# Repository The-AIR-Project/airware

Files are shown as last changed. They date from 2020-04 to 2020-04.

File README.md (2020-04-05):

# AIRware
Files for the AIR project.

#### External Libraries

LiquidCrystal_I2C (https://github.com/fdebrabander/Arduino-LiquidCrystal-I2C-library/blob/master/LiquidCrystal_I2C.h)

#### How To Use

If the software is loaded as is onto the Arduino, and the:
- One button (black, on our design) cycles through age group settings
    - These can only be toggled while ventilation is not in progress
- Potentiometers adjust volume, pressure, and rate settings
    - These can be adjusted at any time
    - Volume measurements are calibrated as explained below
- If the airway is blocked, the servo will draw too much current and a blockage
is predicted (see how to calibrate this below)  

#### Volume Output Characterization

- Record volume outputs at various servo angles
- In `scripts/volume_character.py`, place these values into `raw_vol` and `raw_ang`
- Take the average volume output at each servo angle, place these values into
`vol` and `ang`
- If any validation takes place, place these volumes and servo angles into
`val_vol` and `val_ang`
- Note: the `ang_to_vol` function was determined by fitting a cubic to the
volume output vs servo angle data in Excel

#### Blockage Detection Characterization

- Blockage detection is only implemented in adults right now
- Any adjustments to mechanical design requires recalibration
- To calibrate, output the volume, pressure, and `current_sum` value upon releasing the bag (around line 400 or so)
- Save this data in Excel in the format shown in `current_data.xlsx`, which contains
the most recently-used data for characterization
- Run `scripts/current_character.py` to fit a surface function to the data and output the
coefficients `[a, b, c, d, e, f]`
    - polynomial of the form `z = a + bx + cx^2 + dy + ey^2 + fxy`
- Apply these coefficients in  `predict_current()` function

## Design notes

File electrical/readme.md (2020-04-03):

# Electrical Schematic

`electrical.pdf` contains a simple diagram showing necessary connections for the
electrical aspect of our design.
- The only power requirements is that it's able to supply the Arduino with
7-12V, the servo with 6.8V, and supply up to 3A (anything above 2.5A <i>should</i>
be okay, but we went with 3A to be safe)
    - If you use a different MCU or motor, just make sure you meet its specs of
    course
- The 220 ohm resistors on the LEDs can be any value that works for you
    - the red LED we used should have gotten a larger resistor, which is why
    in the code it is being powered by PWM (it was too bright!)

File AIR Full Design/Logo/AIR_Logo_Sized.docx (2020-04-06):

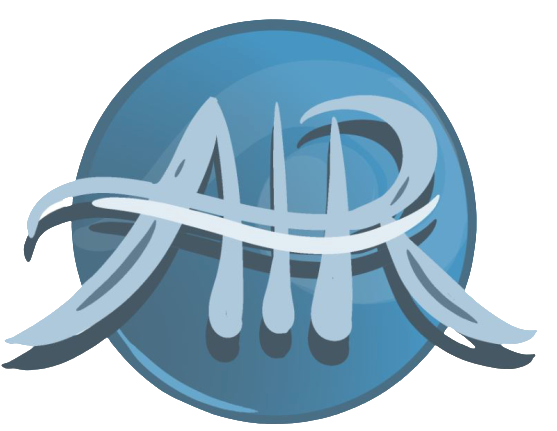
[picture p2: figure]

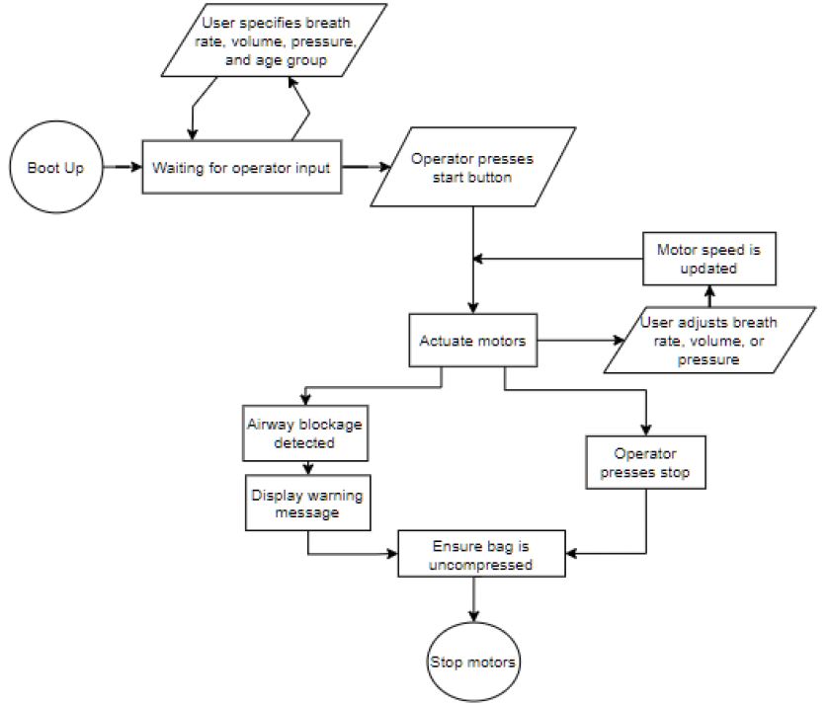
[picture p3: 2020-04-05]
final_code/flowchart.JPG

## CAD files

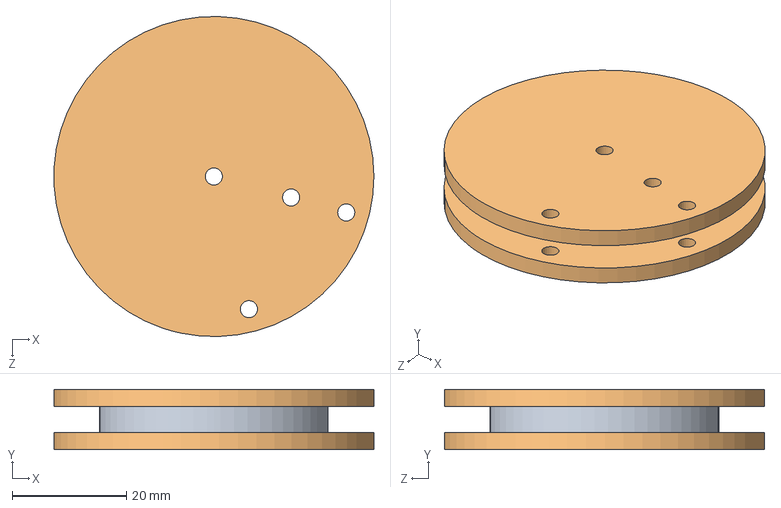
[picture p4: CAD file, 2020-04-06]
AIR Full Design/Spool_Assembly.SLDASM
56.0 x 10.5 x 56.0 mm
Servo_Spool_Inside
Servo_Spool_Outside x 2

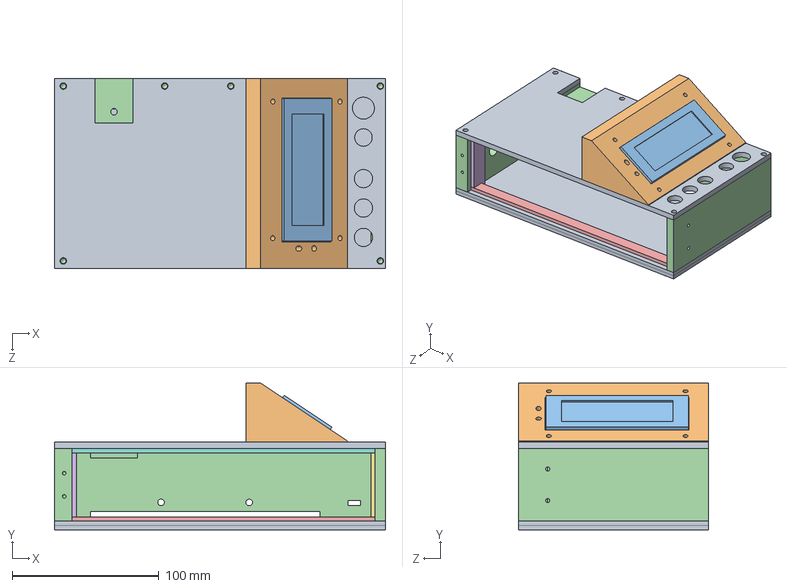
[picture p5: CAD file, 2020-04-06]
AIR Full Design/Control Box V4/Control_Box_V4.SLDASM
225.2 x 100.0 x 129.0 mm
Control Box Top
Screen_Mount
LCD_Screen
Box Frame
Door_Frame_Bottom
Door_Frame_Left
Door_Frame_Right
Door_Frame_Top
Control Box Bottom x 2

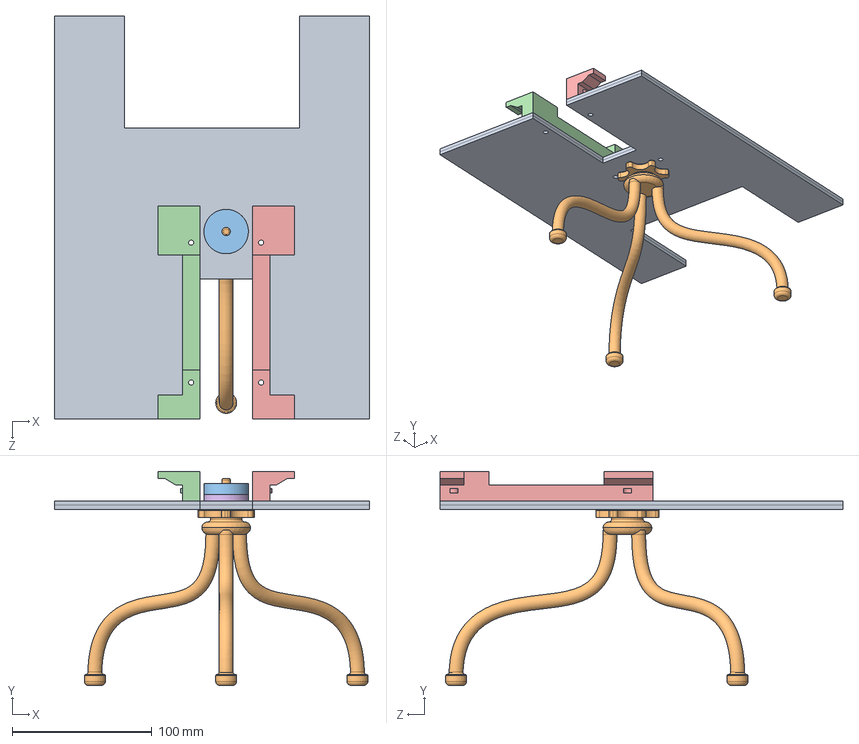
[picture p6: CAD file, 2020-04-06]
AIR Full Design/Mounting Stand/Mount_Interface_Assembly.SLDPRT.SLDASM
225.2 x 153.0 x 288.1 mm
Mount_Interface_Plate x 2
Mount_Interface_Tripod
Mount_Interface_Securement_Disk
Mount_Interface_Finger_Left
Mount_Interface_Finger_Right
Mount_Interface_Spacer

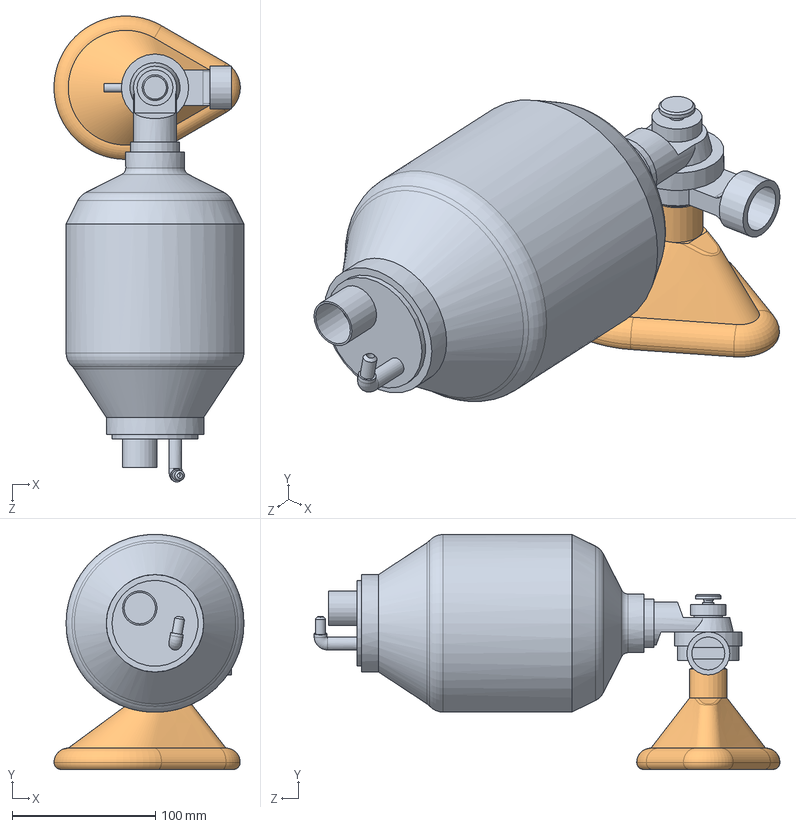
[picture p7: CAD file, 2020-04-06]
AIR Full Design/Bag Valve Mask/Bag_Valve_Mask.SLDASM
132.5 x 163.9 x 325.0 mm
Bag_Adult
Mask_Updated

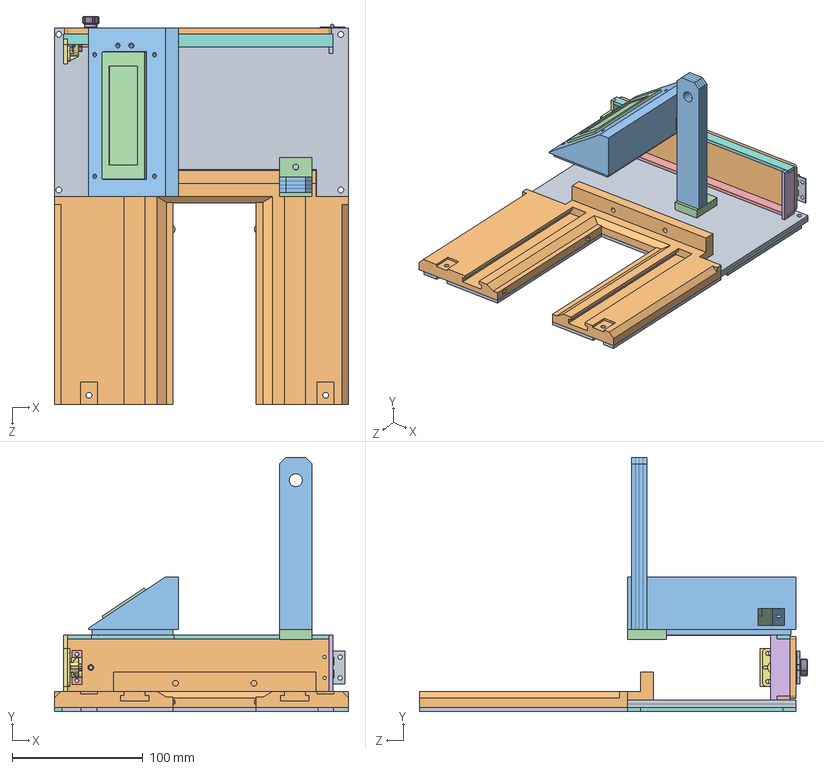
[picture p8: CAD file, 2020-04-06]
AIR Full Design/Base_Structure_Assembly.SLDASM
225.3 x 194.5 x 296.8 mm
Base_Frame_V3
Screen_Mount
LCD_Screen
Door_Frame_Bottom
Door_Frame_Left
Door_Frame_Right
Door_Frame_Top
Control Box Bottom x 2
Door_Hinge
Control_Box_Door
Tensioner End Support_Layer x 4
Tensioner End Support_Bottom
Door_Latch_Strike
Door_Knob_Small
Door_Latch_Plate
Control_Box_Spacer
Frame_Spacer

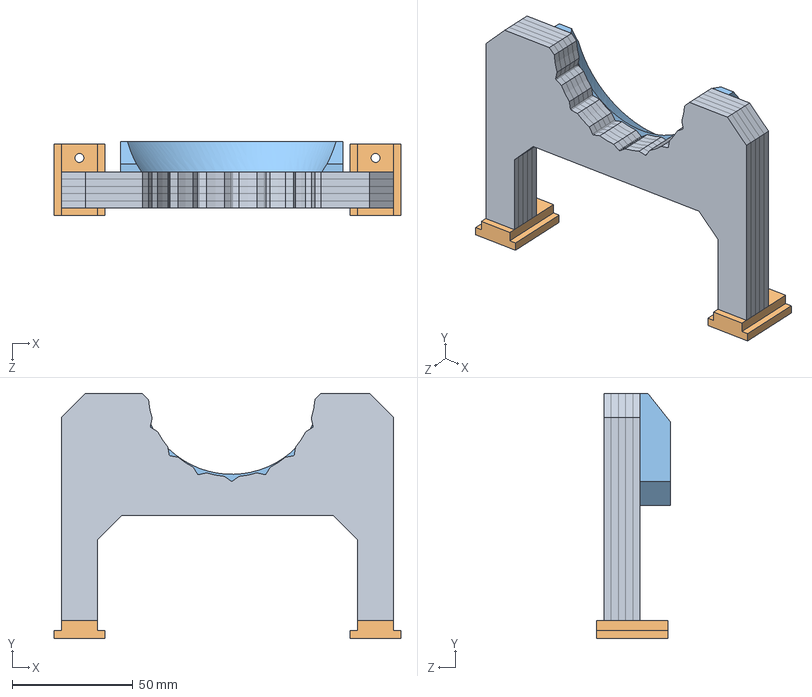
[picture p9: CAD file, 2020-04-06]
AIR Full Design/Back Support Assembly.SLDASM
143.5 x 101.5 x 30.5 mm
Back Support Layer x 5
Back Support Feet x 2
Bag Pullout Support

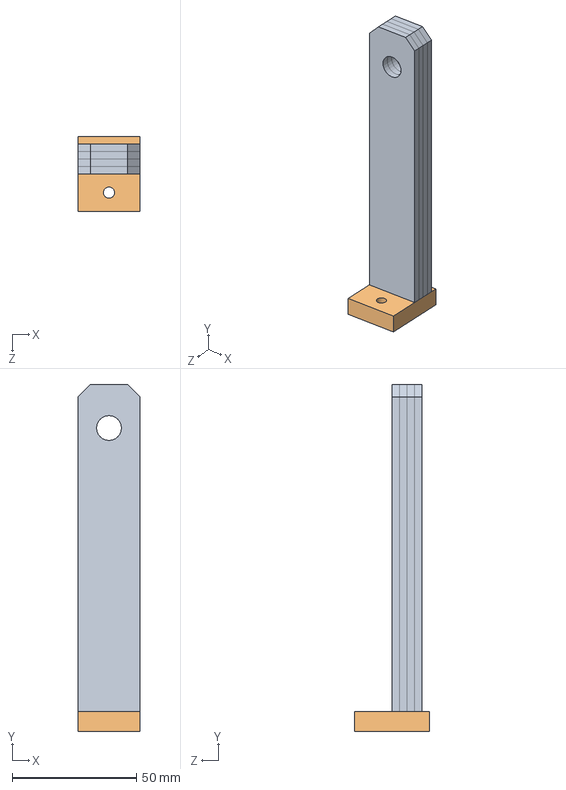
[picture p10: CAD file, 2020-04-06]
AIR Full Design/Tensioner End Support_Assembly.SLDASM
25.0 x 139.5 x 30.0 mm
Tensioner End Support_Layer x 4
Tensioner End Support_Bottom

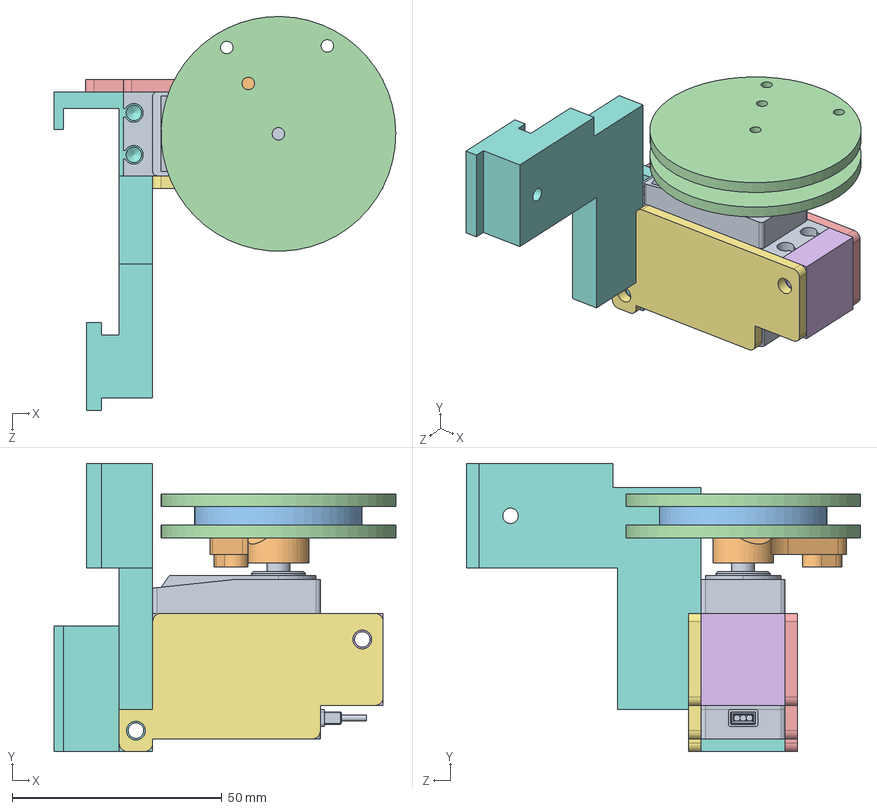
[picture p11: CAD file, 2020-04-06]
AIR Full Design/Servo_Assembly.SLDASM
81.5 x 68.8 x 94.0 mm
Servo
Servo_Arm
Servo_Spool_Inside
Servo_Spool_Outside x 2
Servo_Mount_Plate
Servo_Mount_Block_Top
Servo_Mount_Plate_2
Servo_Mount_Block_Bottom_V4

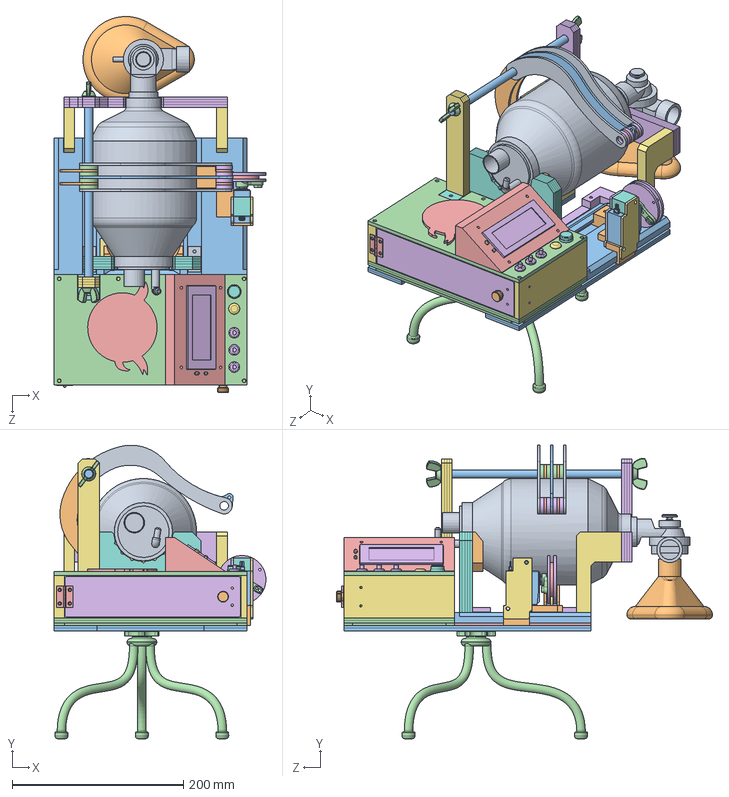
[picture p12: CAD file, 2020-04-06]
AIR Full Design/Full Design_V4.SLDASM
247.2 x 342.4 x 438.7 mm
Bag_Adult
Mask_Updated
Base_Frame_V3
Control Box Top
Screen_Mount
LCD_Screen
Box Frame
Door_Frame_Bottom
Door_Frame_Left
Door_Frame_Right
Door_Frame_Top
Control Box Bottom x 2
Door_Hinge
Control_Box_Door
Tensioner End Support_Layer x 4
Tensioner End Support_Bottom
Door_Latch_Strike
Door_Knob_Small
Door_Latch_Plate
Control_Box_Spacer
Frame_Spacer
Front Support Layer x 4
Front Support Side Legs x 2
Back Support Layer x 5
Back Support Feet x 2
Bag Pullout Support
Servo
Servo_Arm
Servo_Spool_Inside
Servo_Spool_Outside x 2
Servo_Mount_Plate
Servo_Mount_Block_Top
Servo_Mount_Plate_2
Servo_Mount_Block_Bottom_V4
Tensioner_Rod
M10 Wing nut x 2
Logo_Badge__Reference_Only
Potentiometer x 3
Button_Age
Button_Start_Stop
Green_LED
Red_LED
Mount_Interface_Plate x 2
Mount_Interface_Tripod
Mount_Interface_Securement_Disk
Mount_Interface_Finger_Left
Mount_Interface_Finger_Right
Mount_Interface_Spacer
Compression_Arm_Top__Reference_Only x 2
Compression_Arm_Bottom__Referencce_Only x 2
Compression_Arm_Top_With_Connector__Reference_Only
Tensioner_Rod_Spacer x 4
Compression_Arm_Spacer_Thin x 2
Compression_Arm_Spacer x 6
Compression_Arm_Bottom_Connector__Reference_Only

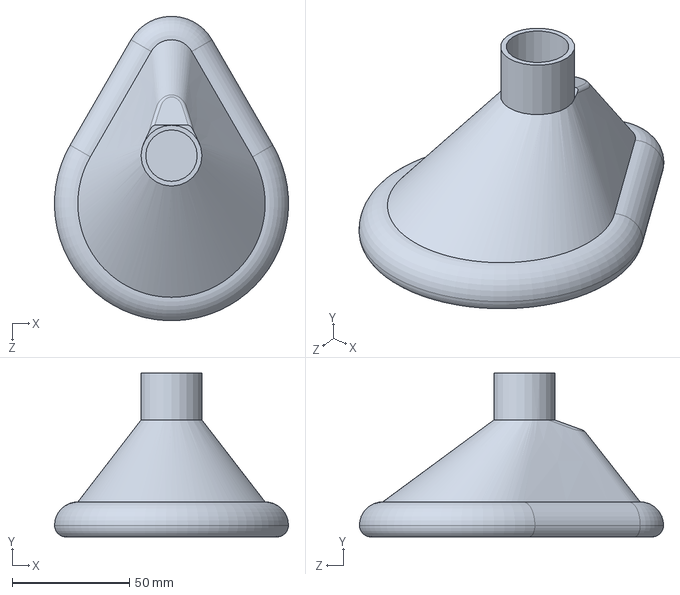
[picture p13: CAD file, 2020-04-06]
AIR Full Design/Bag Valve Mask/Mask_Updated.SLDPRT
99.9 x 70.0 x 129.9 mm

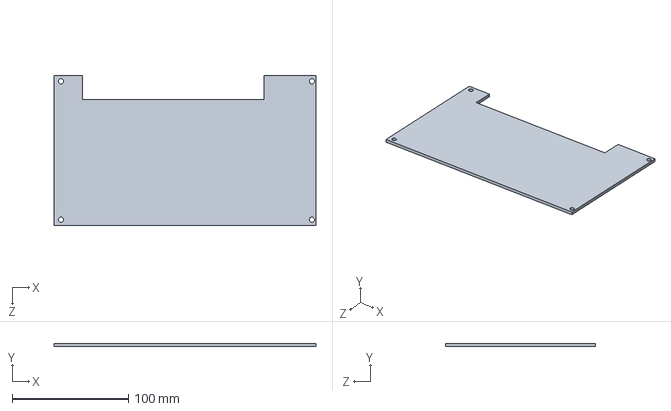
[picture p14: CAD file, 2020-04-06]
AIR Full Design/Control Box V4/Control Box Bottom.SLDPRT
225.2 x 3.00 x 129.0 mm

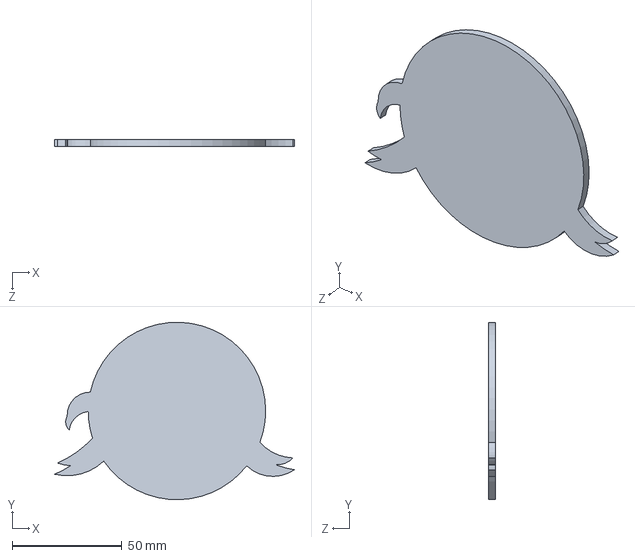
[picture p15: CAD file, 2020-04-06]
AIR Full Design/Logo/Logo_Badge__Reference_Only.SLDPRT
109.6 x 81.0 x 3.00 mm

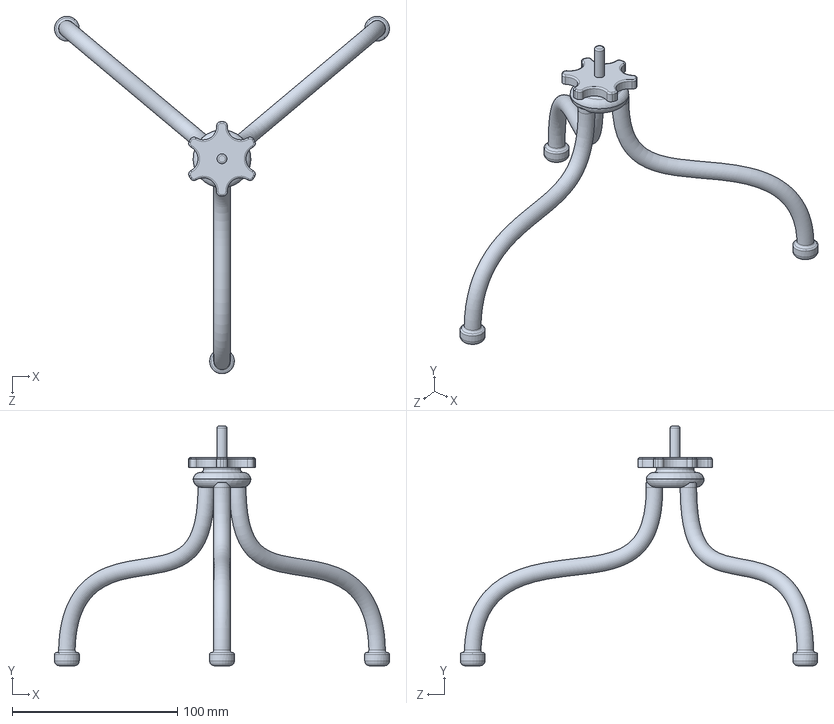
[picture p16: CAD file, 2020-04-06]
AIR Full Design/Mounting Stand/Mount_Interface_Tripod.SLDPRT
202.7 x 145.0 x 216.2 mm

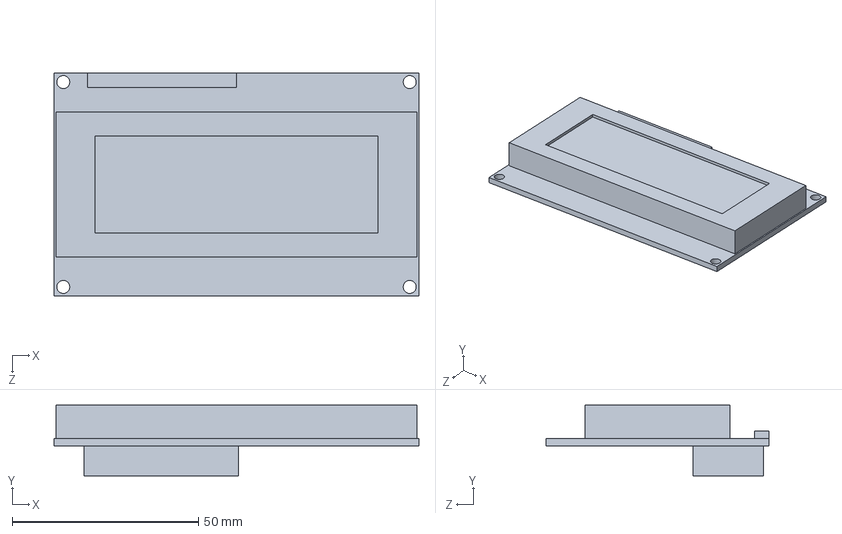
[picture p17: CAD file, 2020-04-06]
AIR Full Design/Stand In Models for Purchased Parts/LCD_Screen.SLDPRT
98.0 x 19.0 x 60.0 mm

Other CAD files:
AIR Full Design/Front Support Assembly.SLDASM
AIR Full Design/AutoCad Files For Reference Parts/Compression Arm Components_4point5mm.dwg
AIR Full Design/AutoCad Files For Reference Parts/Compression Arm Components_3mm.dwg
AIR Full Design/Bag Valve Mask/Bag_Infant.SLDPRT
AIR Full Design/AutoCad Files For Reference Parts/Logo_Badge.DWG
AIR Full Design/Back Support Feet.SLDPRT
AIR Full Design/Back Support Layer.SLDPRT
AIR Full Design/Bag Pullout Support.SLDPRT
AIR Full Design/Bag Valve Mask/Bag_Adult.SLDPRT
AIR Full Design/Base_Frame_V3.SLDPRT
AIR Full Design/Compression_Arm_Bottom_Connector__Reference_Only.SLDPRT
AIR Full Design/Compression_Arm_Bottom__Referencce_Only.SLDPRT
AIR Full Design/Compression_Arm_Spacer.SLDPRT
AIR Full Design/Compression_Arm_Spacer_Thin.SLDPRT
AIR Full Design/Compression_Arm_Top_With_Connector__Reference_Only.SLDPRT
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

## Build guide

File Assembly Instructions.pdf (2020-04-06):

# Automatic Inhalation Resuscitator

# Assembly Instructions

Originally developed by Connor Simmons, Sam Raisbeck, Brian Mao, and Aditya Matam from The University of Waterloo

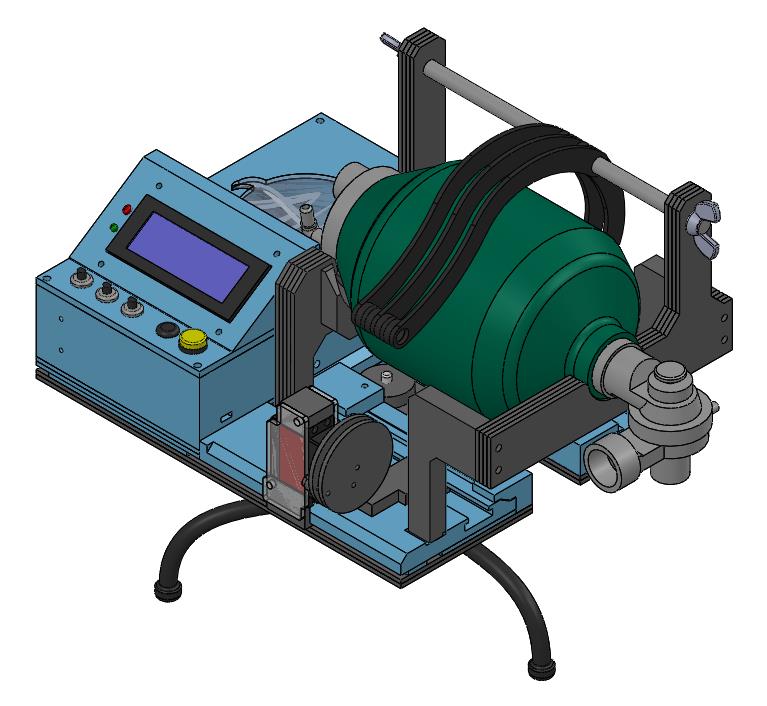
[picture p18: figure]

**Disclaimer: The following assembly instructions are made only as a general guide to construct the version of AIR most recently completed as of April 5, 2020. As this product will be manufactured quickly, components may be modified or exchanged to fit your specific needs. Any modifications made to the design or its components may result in required variations to the assembly.

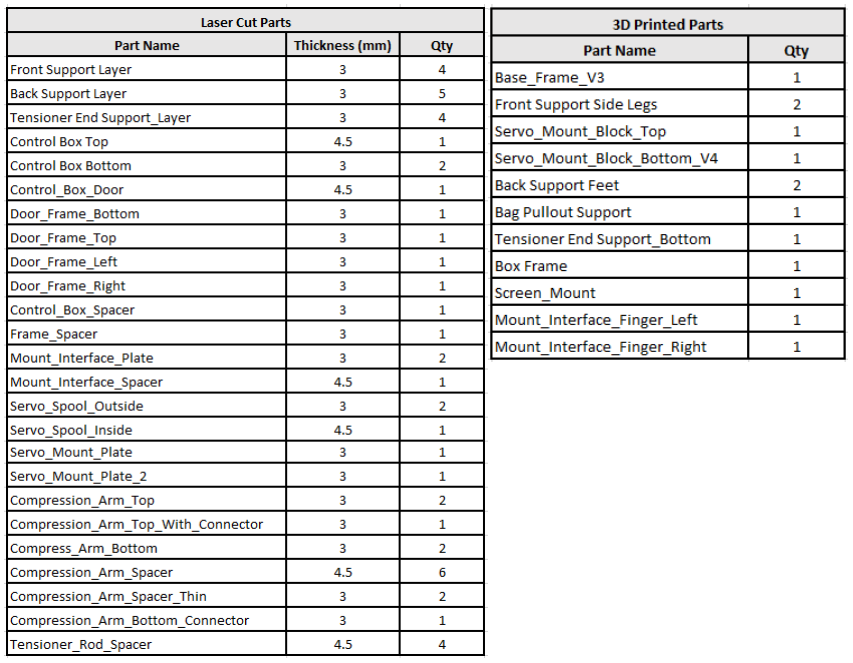
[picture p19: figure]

https://the-air-project.github.io/

Note 1: Please download the entire “Air Full Design” folder, and open the main assembly: “Full Design_V4”

Note 2: Within the provided 3D CAD model, the compression arm models are reference only. This includes the three top arms, two bottom arms, and the bottom arm connector. The dimensions used for the models are reference only and do not fully represent the final manufactured versions. These files are tagged with a “Reference_Only” at the end of the file name.

Note 3: Accurate drawing files for “Reference Only” components can be found in the “AutoCad files” folder. These files are the true manufactured versions for these components. This also includes the logo badge

Note 4: All other components were manufactured according to the dimensions in the CAD model. All dimensions are in mm.

AIR was manufactured using a mixture of 3D printed plastic components, as well as laser cut acrylic. The breakdown of 3D printed vs. laser cut components is listed below. The thickness of acrylic components is also listed, along with a required quantity for each component. The material selections were made with interest to cost and manufacturing time. More complex components were 3D printed, but laser cutting acrylic is often faster and less expensive. Any variations to the materials used is up to manufacturer discretion.

## 1 – Control Box

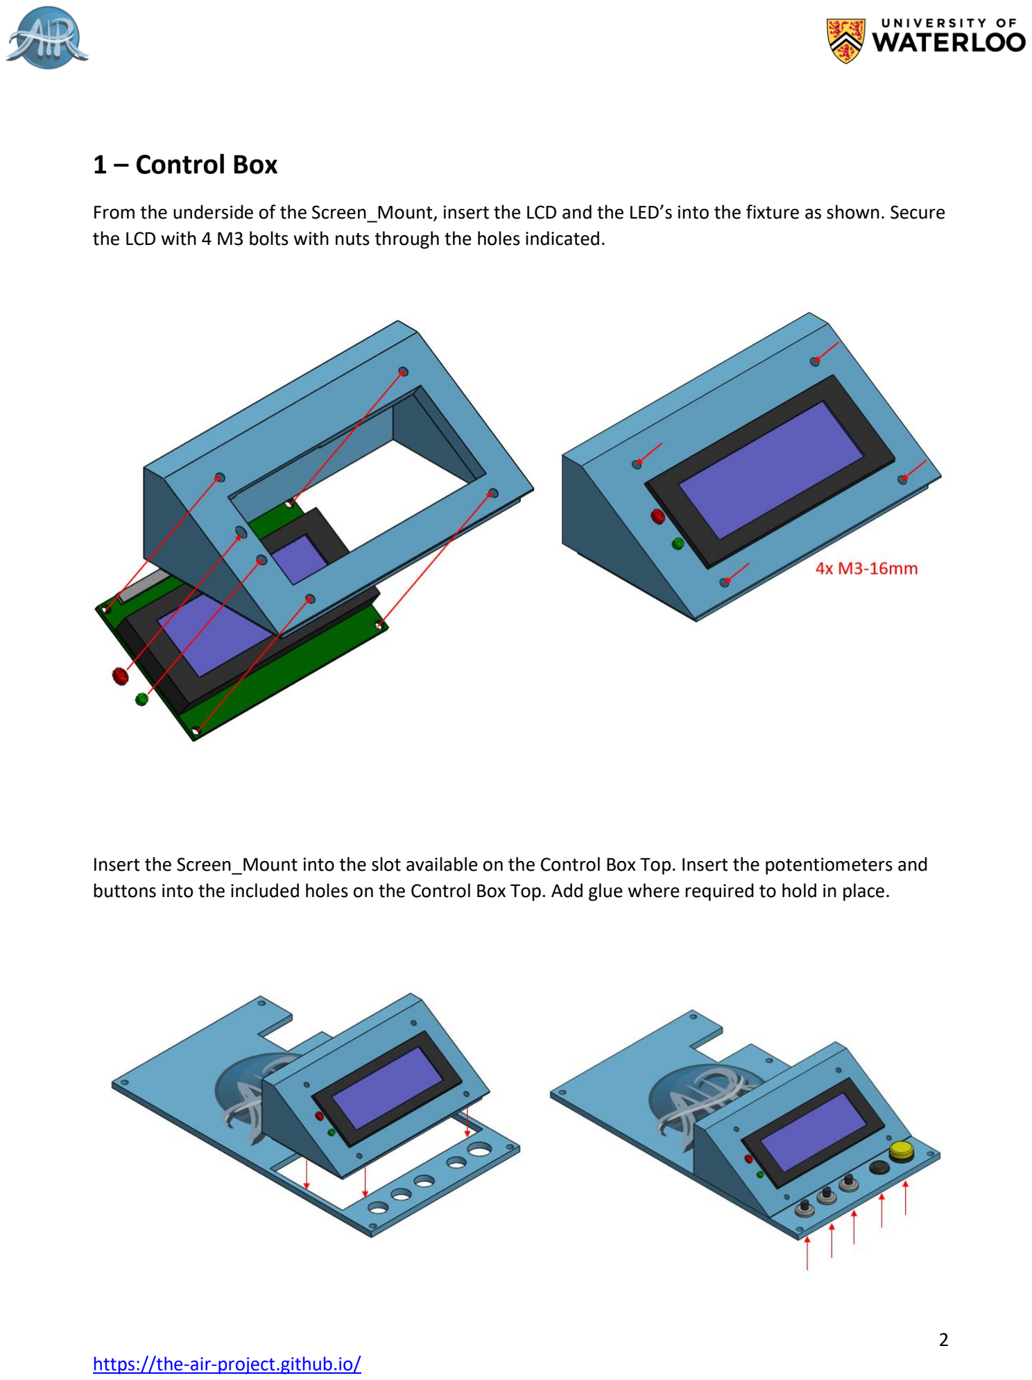
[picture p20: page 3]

From the underside of the Screen_Mount, insert the LCD and the LED’s into the fixture as shown. Secure the LCD with 4 M3 bolts with nuts through the holes indicated.

Insert the Screen_Mount into the slot available on the Control Box Top. Insert the potentiometers and buttons into the included holes on the Control Box Top. Add glue where required to hold in place.

Attach the Control Box Top to the Box Frame through the 6 screw holes indicated.

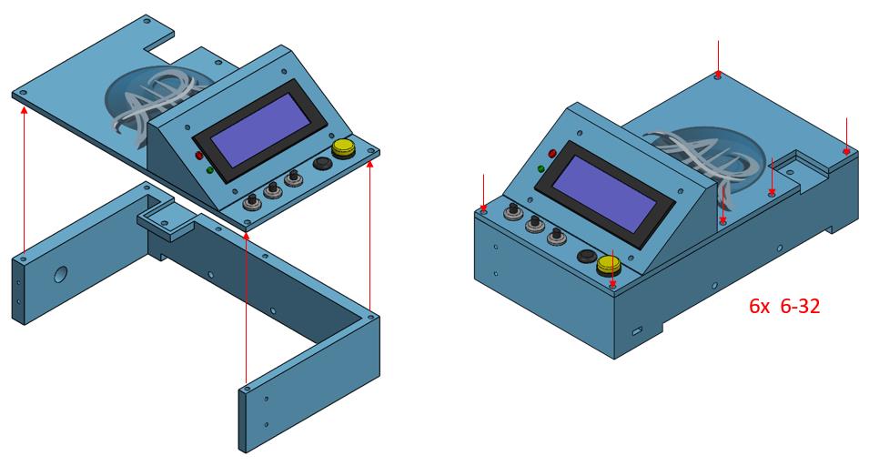
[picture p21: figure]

At this point it is recommended that the control box electronics be fully wired. This includes the connections from the controls to the Arduino, the power supply connector, current, sensor, etc. These connections can be found in our electrical schematic, which is also available for download. A rear view of the control box is included below to indicate the use for the cut-outs on the box frame

Attach 2 layers of the Control Box Bottom in the manner shown to the underside of the control box, through the 4 screw holes indicated.

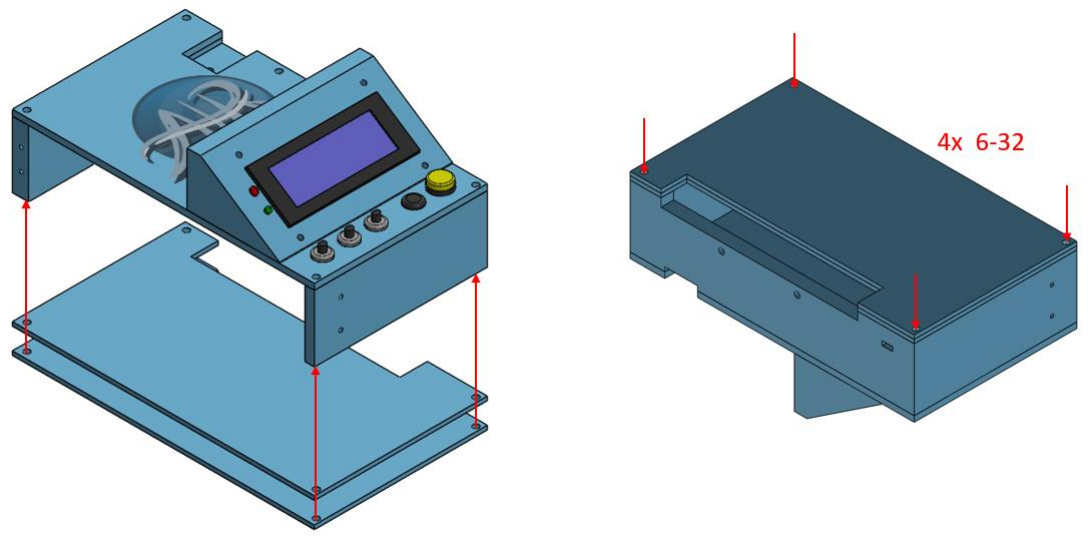
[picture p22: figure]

Place the Door_Frame_Bottom inside the control box, 4.5mm back from the edge of the Control Box Bottom. Add glue where required to hold in place. Repeat for the Door_Frame_Left, Door_Frame_Right, and Door_Frame_Top. If the bottom frame was installed correctly, the remaining frame pieces should fit together nicely with their included cut-outs. Check the placement and orientation of all pieces before

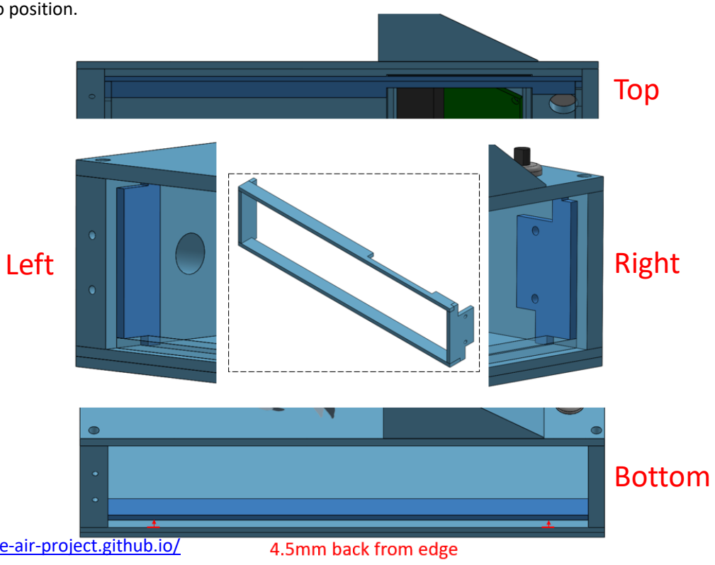
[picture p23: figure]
Left; Right; Top; Bottom

gluing into position.

Place the Door_Latch_Plate inside the control box on the Door_Frame_Left, and secure from the outside of the control box through the indicated screw holes with 2 M3 bolts with nuts.

On the Control_Box_Door, secure the Door_Latch_Strike using 2 M3 bolts, with nuts. Secure the Door_Knob_Small from the other side through the door with a nut. Attach one side of the Door_Hinge to the door with 2 M3 bolts, with nuts. Then, attach the other side of the hinge to the control box with 2 screws. All bolt heads should be on the outside of the door.

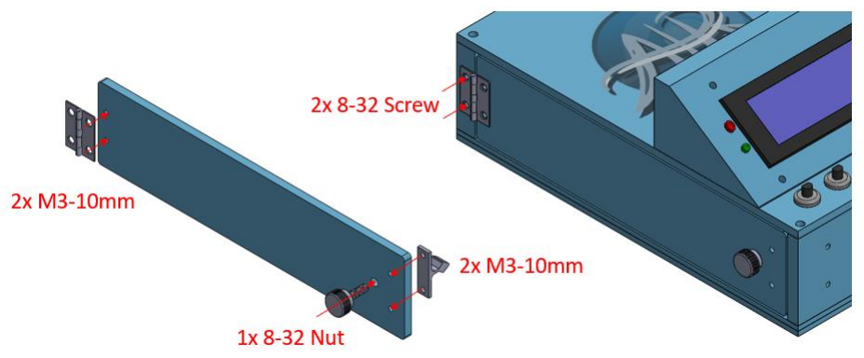
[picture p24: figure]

Available for download are our personal AIR logo and the AutoCad file for the logo badge. If willing, print and cut out the logo, and place on the control box with a little amount of glue. Then, place the logo badge overtop to protect the logo and provide a 3D effect. Add small drops of glue periodically around the perimeter of the badge once in place to secure. Only use small amounts around the outside as excess glue may seep underneath and effect the logo presentation.

The logo is sized properly in the AIR_Logo_Sized document.

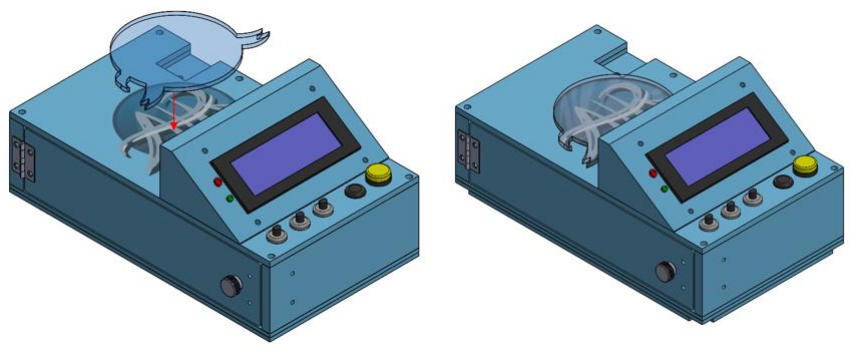
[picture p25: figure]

## 2 – Back Support Assembly

Place 5 Back Support Layers together, add glue where required to hold in place. Take special note that the support is NOT symmetric. The two top edges have slightly different lengths as indicated

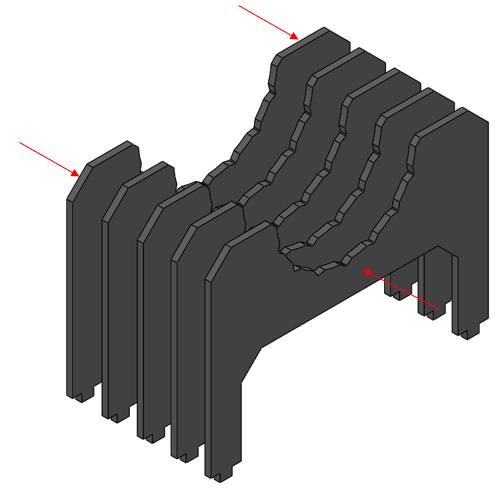
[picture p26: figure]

Take the combined layers and attach the 2 Back Support Feet by fitting the protruding nub on the bottom of the support legs into the notch on the feet as indicated. Note the orientation of the feet in relation to the edge lengths of the top of the support. Add glue to the notch to fully secure.

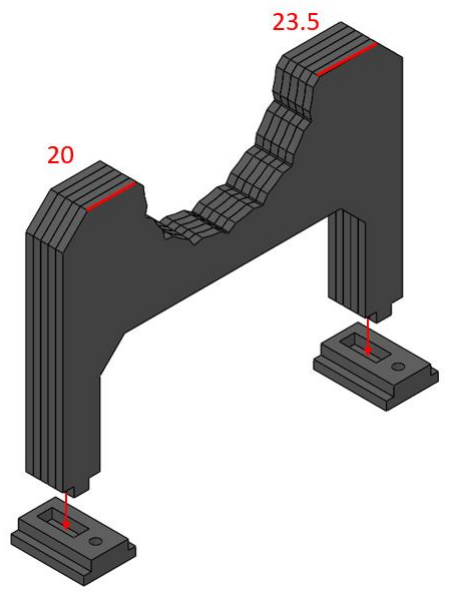
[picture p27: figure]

Attach the Bag Pullout Support to the support layers as indicated, add glue where required to hold in place. The flat edges at the top of the Pullout Support should be aligned with the top edge of the support layers as shown highlighted in blue.

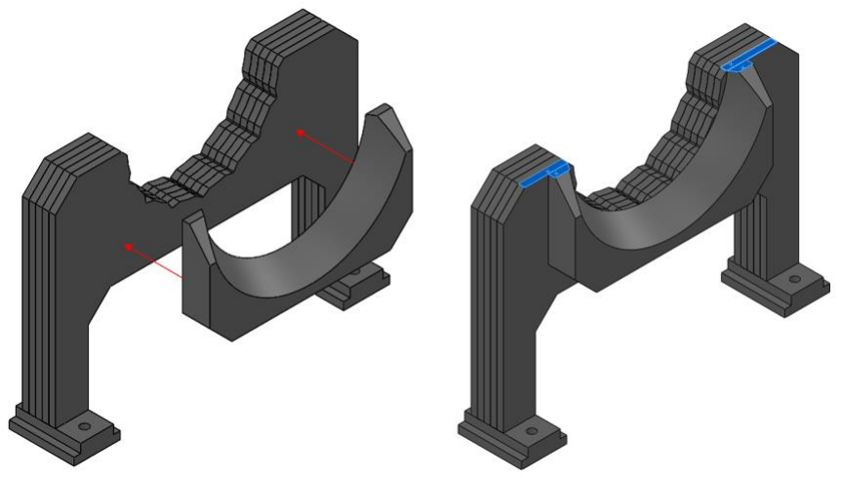
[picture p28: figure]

## 3 – Servo Assembly

Place the Servo_Mount_Block_Top and Servo_Mount_Block_Bottom_V4 on the servo in the positions shown. Secure in place using 4 screws in the locations shown, but DO NOT tighten fully.

Add the Servo_Mount_Plate in the position and orientation shown. Secure to the servo mount blocks in the indicated screw locations. Again, DO NOT tighten fully. Repeat for Servo_Mount_Plate_2. Once both plates are secure, go back and tighten all 8 screws.

To assemble the spool, take the servo arm and attach to a Servo_Spool_Outside, aligning the center of the servo arm with the center hole on the spool, and the furthest hole on the servo arm with the singular hole near the rim of the spool. Secure the arm using only the 1 screw provided with the arm in the hole furthest from the center. If a screw was not provided, an M3 bolt can be used

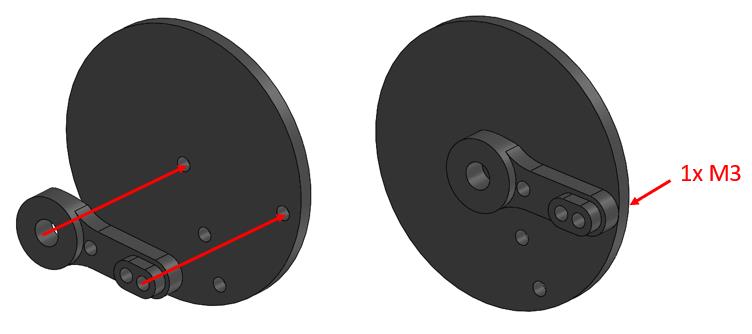
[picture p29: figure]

Next, place the Servo_Spool_Outside and servo arm pair together with another Servo_Spool_Outside on either side of a Servo_Spool_Inside. Align the set of 3 in-line holes as indicated. Secure the spool components together by 2 M3 bolts, with nuts. The bolt closer to the center will go through all 3 layers. The bolt near the outer rim goes through only the 2 outer spool layers.

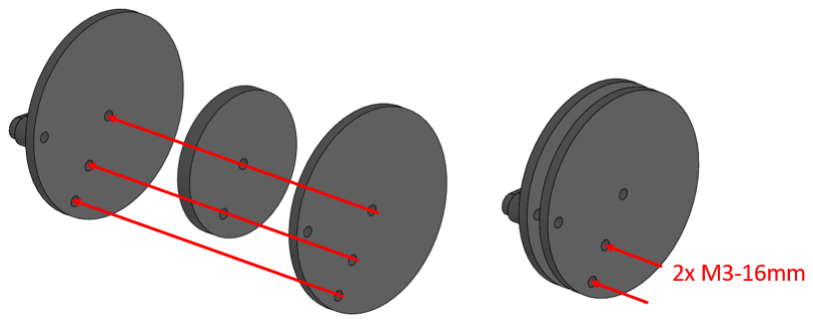
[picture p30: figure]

Attach the servo spool to the servo using the servo arm. Align the large center hole on the servo arm with the shaft of the servo. Secure the spool to the servo using an M3 bolt through the center hole on the spool as shown.

## 4 – Tensioner End Support Assembly

Place 4 Tensioner End Support Layers together, add glue where required to hold in place

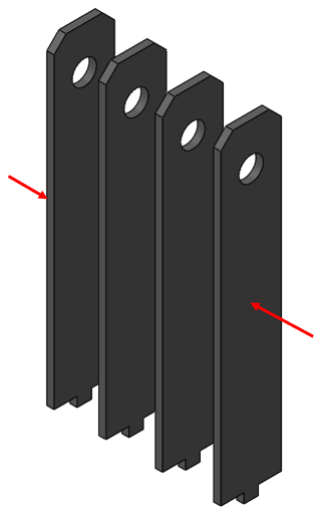
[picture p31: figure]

Take the combined layers and attach the Tensioner End Support_Bottom by fitting the protruding nub on the bottom of the support legs into the notch on the foot as indicated. Add glue to the notch to fully secure.

## 5 – Full Frame Assembly

Take the Base_Frame_V3 and insert into the open slot at in the front of the control box assembly from the underside. Secure the frame to the box using 2 bolts through the indicated holes and attach with nuts from the inside of the control box.

Insert the Tensioner End Support Assembly into the slot on the top of the control box. Secure to the box using 1 bolt through the Tensioner Support Assembly base, and attach a nut from the inside of the control box.

Take the Back Support Assembly and slide the support feet into the channels on the Base Frame as shown. Slide the support all the way to the end of the channel, or the approximate distance for the size of your Bag Valve Mask being used. Slide the Servo Assembly into the left side channel as shown. Insert the cable for the servo through the small square hole on the side of the control box.

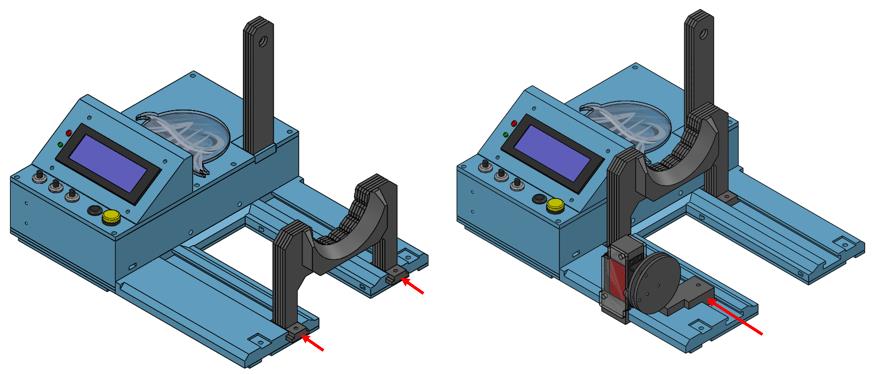
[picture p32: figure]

Take 2 Front Support Side Legs and insert them into the indented slots at the front of the Base Frame. Secure from the underside using 2 screws.

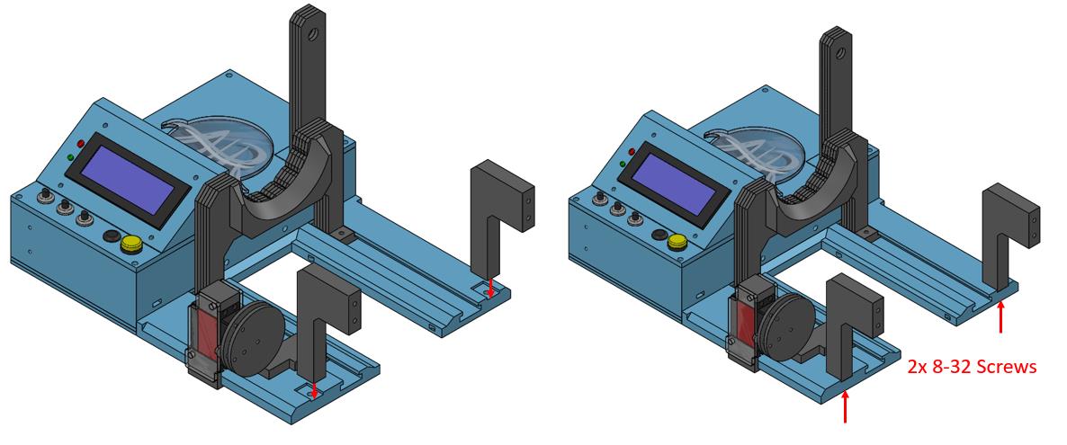
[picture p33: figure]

Place 4 Front Support Layers together against the Front Support Side Legs and secure from the front using 4 screws.

Align the Control Box Spacer and the Frame Spacer as shown on the underside of the frame. Add glue where required to hold in place

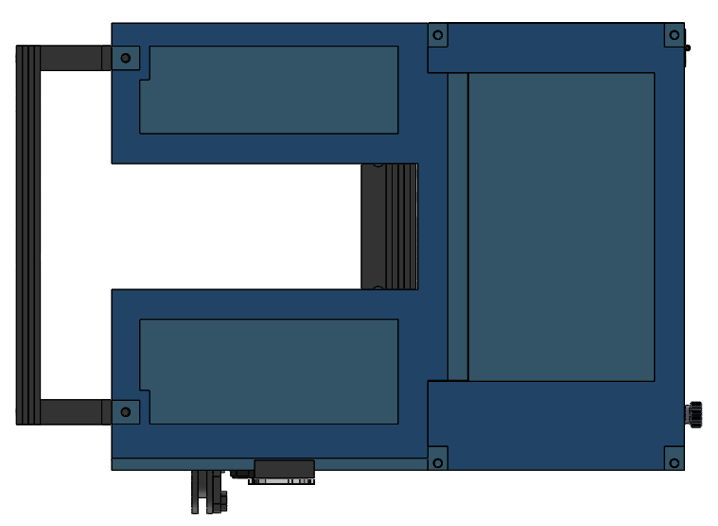
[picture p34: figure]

## 6 – Compression Arms

For the top compression arms, combine them together with the spacers only on the bottom side in the pattern shown. The compression arms must be arranged so the arm with the additional connector nub is in the middle, and the two regular arms the outside. In between, use 4 Compression_Arm_Spacers and 2 Compression_Arm_Spacer_Thin in the pattern indicated. Ensure all holes at both ends are aligned concentrically. Add glue where required to hold in place.

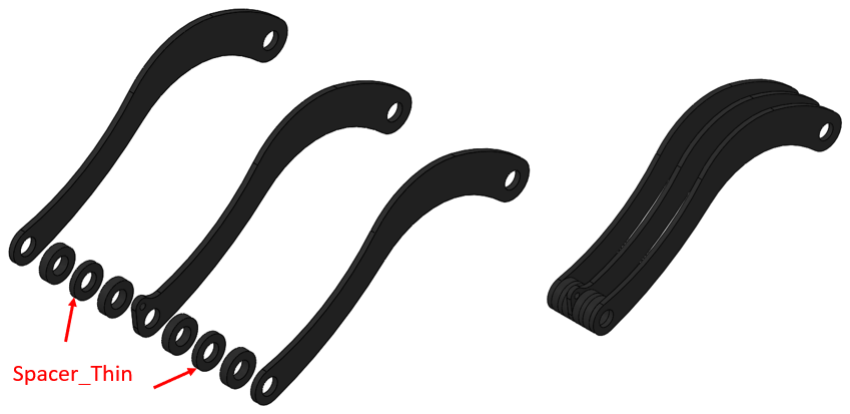
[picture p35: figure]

For the bottom compression arms, combine them together with the spacers only on the bottom side in the pattern shown. The compression arms are arranged on the outside, with the spacers and the additional connector in between. Use 2 Compression_Arm_Spacers and the connector piece in the pattern indicated. Ensure all holes at both ends are aligned concentrically. Add glue where required to hold in place.

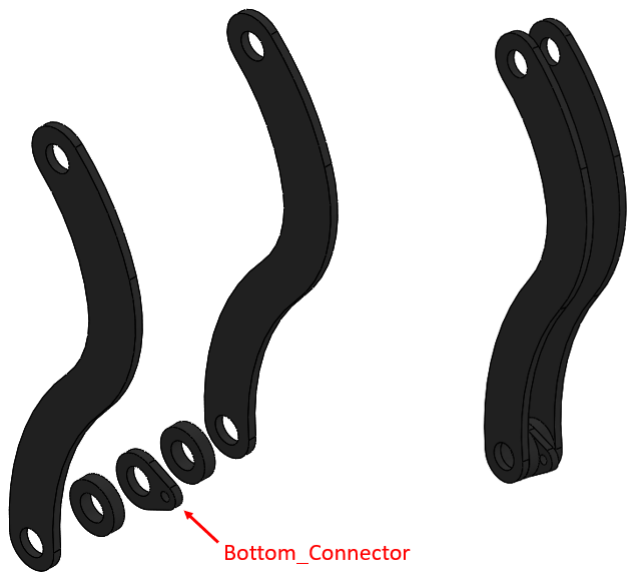
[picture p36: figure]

Slide the Tensioner_Rod through the hole in the Front Support Assembly. Add an O-ring before adding the combination of compression arm assemblies and spacers as shown. The 3 top compression arms and 2 bottom compression arms fit together at the open ends as shown, with a Tensioner_Rod_Spacer in between each arm (highlighted in dark blue between the black arms). It is important not to glue these spacers as they need to be free to rotate relative to each.

Note: The tensioner rod is 3/8” Aluminum, with 1-inch long threaded sections at the ends (3/8-16 thread)

Add another O-ring after the compression arm assemblies, and feed the tensioner rod though the tensioner end support assembly. Secure the rod in place at both ends with 2 wing nuts.

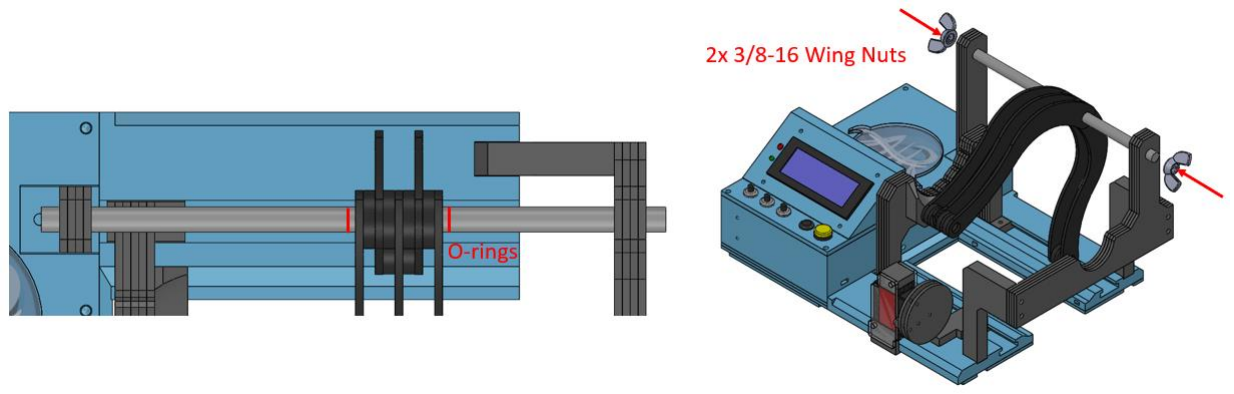
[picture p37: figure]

## 7 – Mount Interface Assembly

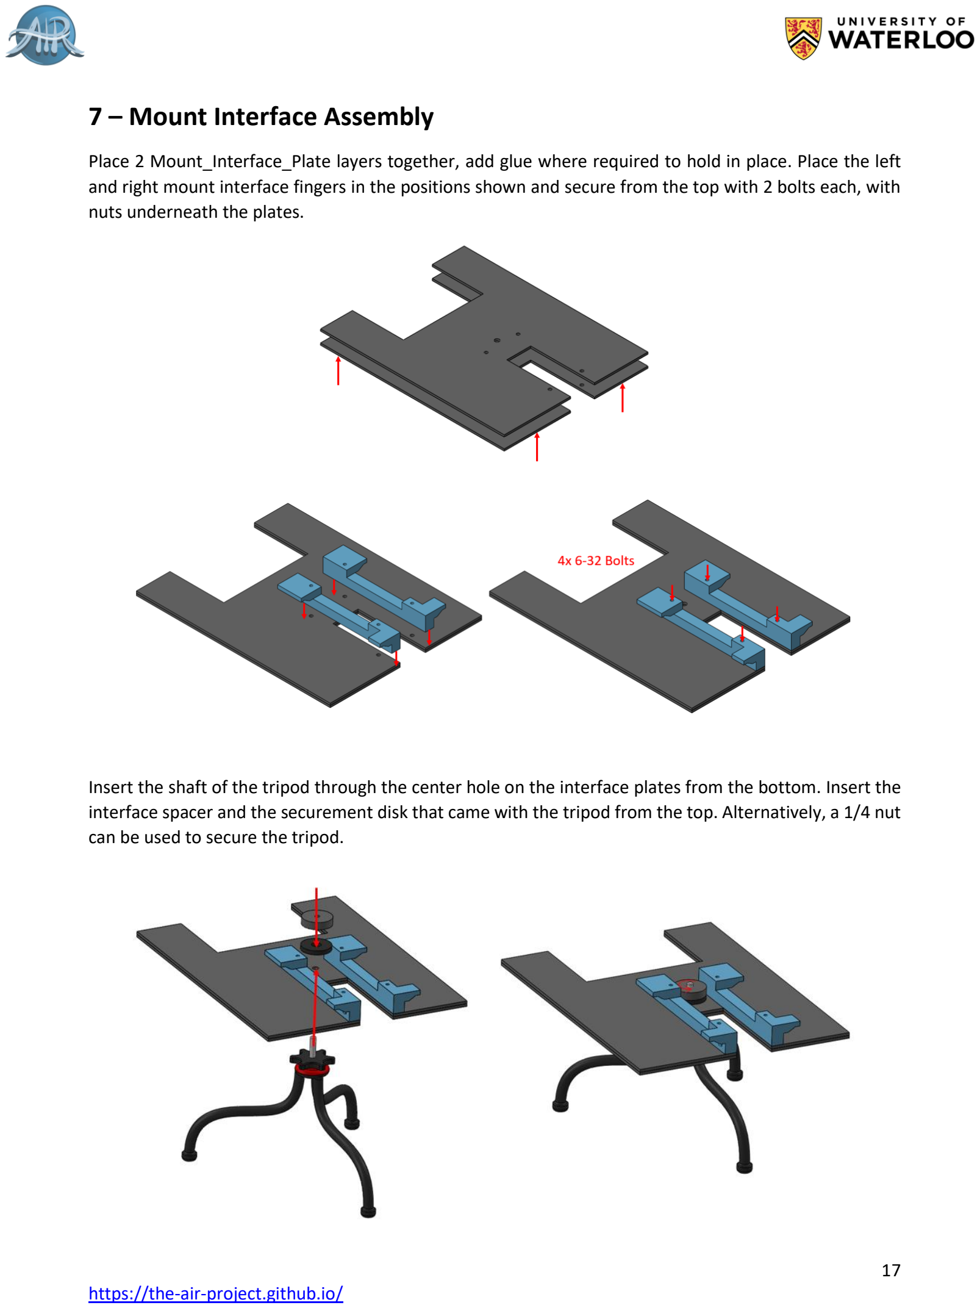
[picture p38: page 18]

Place 2 Mount_Interface_Plate layers together, add glue where required to hold in place. Place the left and right mount interface fingers in the positions shown and secure from the top with 2 bolts each, with nuts underneath the plates.

Insert the shaft of the tripod through the center hole on the interface plates from the bottom. Insert the interface spacer and the securement disk that came with the tripod from the top. Alternatively, a 1/4 nut can be used to secure the tripod.

## 8 – Getting Ready to Use

To attach the compression arms to the servo spool, nylon wire is used. Tie one end of a piece of nylon wire around the connector on the lower compression arm set. Tie the other end of the wire around the outermost screw on the servo spool, with the spool in the approximate orientation shown. Repeat this for the upper compression arms, except instead of tying the wire directly to the arm connector, tie it to one end of the hook as shown. The other end of the hook can then be fed through the connector on the middle upper compression arm.

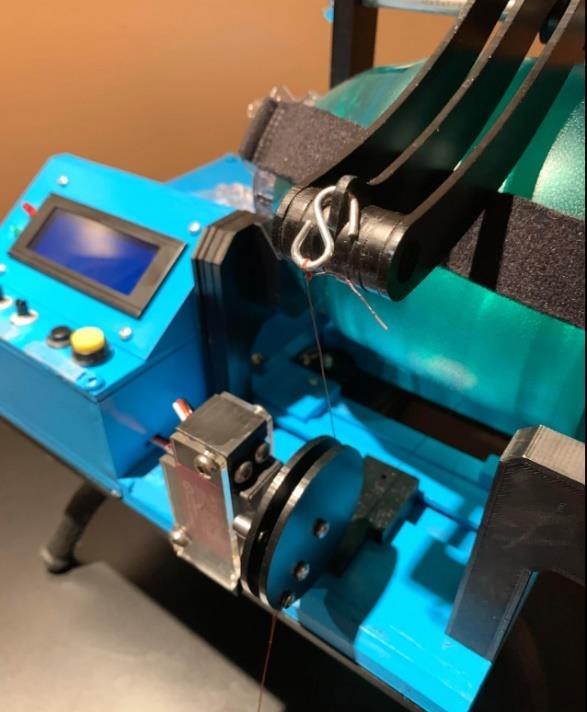
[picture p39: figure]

Remove the hook, lift and rotate the top compression arms out of the way. Place the Bag Valve Mask inside the device as shown. The upper arms can then be lowered, and the hook can be re-attached.

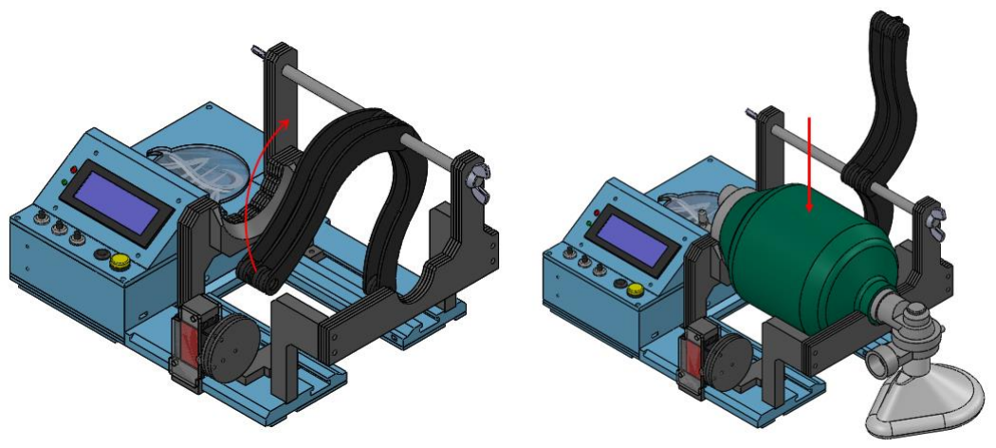
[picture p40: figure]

It is important the wires connecting the compression arms to the servo spool are taught when the bag is fully uncompressed and the servo is in its start position. Some trial and error by the user will be required during setup to achieve proper results. It is recommended that the device be turned on and run through 1 compression to see the start/stop location of the servo. Then, with the device off, the servo spool should be carefully removed using the center screw and rotated to ensure the wires are taught in this position before reattachment. Starting from the approximate servo orientation mentioned previously should help. Note that the servo will be rotating clockwise form this view during compression.

If a user would like to attach the mounting interface, simply slide it into place on the frame as shown. Bend the legs of the tripod as required to adjust height and positioning of the device. The mount can be removed in the same fashion.

These assembly instructions are a guide only. They are also subject to change due to any changes in the design or its components. Use own discretion when implementing changes.

Please see the demonstration video on our website for proper operation: https://the-air-project.github.io/

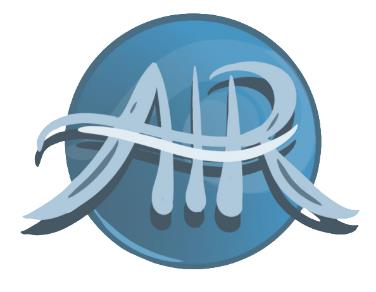
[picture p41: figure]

# Automatic Inhalation Resuscitator

# Assembly Instructions

Originally developed by Connor Simmons, Sam Raisbeck, Brian Mao, and Aditya Matam from The University of Waterloo

## Bill Of Materials

** If manufactured in large quantities, final device cost is expected to decrease, due to purchasing components such as fasteners in bulk quantities.

## Revision Table

Revision Date | Revision Description | Relevant Page Number(s)
06/04/2020 | Updating BOM | 21

** The following revision table will be used by members of the AIR team if updates to our manufacturing and assembly are made. The document will be replaced on our organization webpage with the included revisions. Feel free to use the table to keep track of your own changes if desired.

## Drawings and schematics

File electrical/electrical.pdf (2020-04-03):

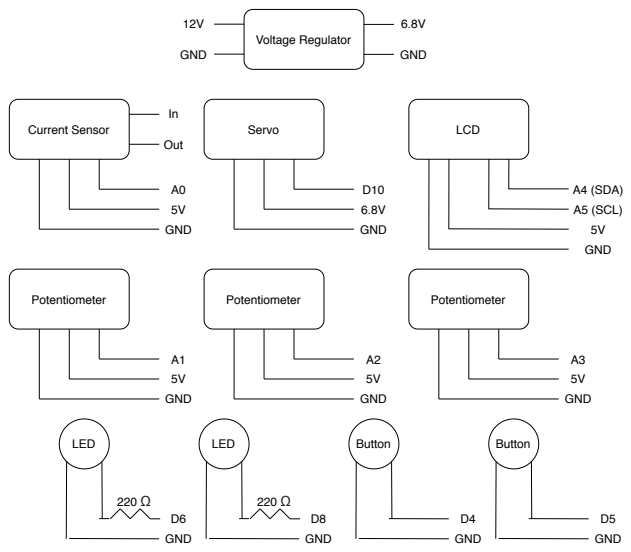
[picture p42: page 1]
Servo; LCD; Potentiometer; GND; A4 (SDA); A5 (SCL); LED; Button; Current Sensor; Out; Voltage Regulator

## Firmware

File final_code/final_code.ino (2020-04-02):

#include <Servo.h>
#include <LiquidCrystal_I2C.h>
#include "constants.h"

// Map from 0, 1024 to -radius, radius
// indices are volume, pressure, rate radii
const int8_t pot_map_radius[3] = {5, 5, 5};

// array shapes are [age group][parameter]
// order is adult, child, infant and volume, pressure, rate
const uint16_t nom_vals[3][3] = {{500, 300, 25}, {5, 5, 5}, {12, 25, 50}};
const uint8_t val_inc[3][3] = {{10, 5, 1}, {1, 1, 1}, {1, 1, 2}};

// base timing for adult, child, infant breaths
const uint16_t base_delays[3] = {950, 550, 200};

// constant strings for LCD
const char clear_value[] = "        ";
const char *setting_titles[3] = {"Volume: ", "Pressure: ", "Breath Rate: "};
const char *age_titles[3] = {"Adult", "Child", "Infant"};
const char *unit[3] = {" mL", "/10", " br/m"};

// Globals
bool ventilating = false;
bool time_to_squeeze = true;
bool time_to_release = true;
long squeeze_time = -100;
long release_time = -100;
bool compression_state = 0;
bool halt = false;
bool warn_user = false;

bool can_read_age_button = true;
long age_button_time = -100;       // time age button was clicked 
bool can_read_start_button = true;
long start_button_time = -100;     // time start button was clicked

int8_t pot_vals[3] = {0, 0, 0};
uint8_t age_state = 0;             // 0, 1, 2 -> adult, child, infant

// for the warning message
long red_led_flash = 0;
bool red_led_flash_on = false;

/*
Sensitivity array is holding the sensitivy of the  ACS712
current sensor models. 
Do not change. All values are from page 5  of data sheet          
*/
double sensitivity[] ={
          0.185,// for ACS712ELCTR-05B-T
          0.100,// for ACS712ELCTR-20A-T
          0.066// for ACS712ELCTR-30A-T
         }; 
double voltage;
double current_sum = 0;

Servo servo;
LiquidCrystal_I2C lcd(0x27, 20, 4);


///// FUNCTIONS /////


int map_pot_val(uint16_t unmapped_pot_val, int8_t pot_index)
{
  // map the potentiometer value to the desired radius
  return map(unmapped_pot_val, 0, 1024, pot_map_radius[pot_index], -pot_map_radius[pot_index]);
}

int16_t map_servo_pos(int16_t pos)
{
  // map the servo position to 180->0
  return map(pos, 0, MAX_SERVO_POS, 180, 0);
}

void lcd_update(uint8_t pot_index)
{
  // update the desired parameter on the lcd
  lcd.setCursor(LCD_H_SPACING - 1, pot_index + POT_LCD_OFFSET);
  lcd.print(clear_value);
  lcd.setCursor(LCD_H_SPACING, pot_index + POT_LCD_OFFSET);
  int16_t val = nom_vals[pot_index][age_state] + val_inc[pot_index][age_state] * pot_vals[pot_index];
  lcd.print(val); // UPDATE THIS TO BE MAPPED VALUE
  lcd.print(unit[pot_index]);
}

void lcd_update_age()
{
  // update the age setting on the lcd
  lcd.setCursor(LCD_H_SPACING - 1,0);
  lcd.print(clear_value);
  lcd.setCursor(LCD_H_SPACING, 0);
  lcd.print(age_titles[age_state]);
  for (uint8_t i = 0; i < 3; ++i)
  {
    // update the parameters, since age changed
    lcd_update(i);
  }
}

void lcd_startup()
{
  // lcd startup message
  lcd.clear();
  lcd.setCursor(8, 0);
  lcd.print("AIR");
  lcd.setCursor(0,2);
  lcd.print("Automatic Inhalation");
  lcd.setCursor(4,3);
  lcd.print("Resuscitator");
}

void lcd_init_titles()
{
  // initialize the lcd titles
  lcd.clear();
  lcd.setCursor(0, 0);
  lcd.print("Age Group:");
  lcd.setCursor(0, 1);
  lcd.print("Volume:");
  lcd.setCursor(0, 2);
  lcd.print("Pressure:");
  lcd.setCursor(0, 3);
  lcd.print("Breath Rate:");
}

void lcd_init()
{
  // initialize the entire lcd
  lcd_init_titles();
  lcd_update_age();
}

void lcd_warn()
{
  // show the warning message on the lcd
  lcd.clear();
  lcd.setCursor(2, 0);
  lcd.print("BLOCKAGE DETECTED");
  lcd.setCursor(0, 1);
  lcd.print("Press yellow button");
  lcd.setCursor(0, 2);
  lcd.print("to cancel warning.");
}

void check_pot_vals()
{
  // check potentiometer values
  // if one has changed, update the lcd
  for (uint8_t i = 0; i < 3; ++i)
  {
    if (map_pot_val(analogRead(i + POT_PIN_OFFSET), i) != pot_vals[i]) 
    {
      pot_vals[i] = map_pot_val(analogRead(i + POT_PIN_OFFSET), i);
      lcd_update(i);
    }
  }
}

void check_age_setting()
{
  // check the age button, update age_state if changed
  if (!digitalRead(P_SETTING_BUTTON) && can_read_age_button) 
  {
    age_button_time = millis();
    can_read_age_button = false;
    age_state = (age_state + 1) % 3;
    lcd_update_age();
  }
}

void check_start_stop()
{
  // check if the start/stop button was clicked
  if (!digitalRead(P_START_BUTTON) && can_read_start_button) 
  {
    // cancel the warning if in place
    if (warn_user)
    {
      red_led(true);
      warn_user = false;
      lcd_init();
    }
    else
    {
      // start or stop ventilation
      start_button_time = millis();
      can_read_start_button = false;
      ventilating = !ventilating;
      red_led(!ventilating);
      green_led(ventilating);
    }
  }
}

bool check_halt()
{
  // check if operation was halted
  if (ventilating && warn_user)
  {
    return true;
  }
  bool was_ventilating = ventilating;
  check_start_stop();
  if (was_ventilating && !ventilating)
  {
    return true;
  }
  return false;
}

uint8_t get_servo_delay()
{
  // get the servo delay based on potentiometer value
  uint16_t des_delay = nom_vals[PRES][age_state];
  des_delay += val_inc[PRES][age_state] * pot_vals[PRES];
  des_delay = map(des_delay, nom_vals[PRES][age_state] - pot_map_radius[PRES] * val_inc[PRES][age_state], nom_vals[PRES][age_state] + pot_map_radius[PRES] * val_inc[PRES][age_state], MIN_SPEED, MAX_SPEED);
  return des_delay;
}

void drive_servo(uint16_t desired_pos)
{
  // drive the servo to its desired position
  uint16_t servo_pos = servo.read();

  // bag release direction
  if (servo_pos < desired_pos)
  {
    for (int16_t pos = servo_pos; pos < desired_pos; pos += 1) {
      halt = check_halt();
      if (halt)
      {
        break;
      }
      servo.write(pos);  
      delay(6);
    }
  }
  
  // bag squeeze direction
  else 
  {
    for (int16_t pos = servo_pos; pos > desired_pos; pos -= 1) {
      halt = check_halt();
      if (halt)
      {
        break;
      }
      servo.write(pos);
      update_current();
      uint8_t del = get_servo_delay(); 
      delay(del);
    }
  }
}

uint16_t get_ms_per_breath()
{
  // get breath rate given potentiometer value
  uint8_t breath_per_min = nom_vals[RATE][age_state] + val_inc[RATE][age_state] * pot_vals[RATE];
  return round(1000 / (breath_per_min / 60.0));
}

uint16_t vol_to_ang(uint16_t vol)
{
  // desired volume to servo angle formula, empirically determined
  return 4.89427e-7 * pow(vol, 3) - 8.40105e-4 * pow(vol, 2) + 0.64294*vol + 28.072327;
}

void red_led(bool on)
{
  // turn on/off red LED
  analogWrite(P_RED_LED, on ? 5 : 0);
}

void green_led(bool on)
{
  // turn on/off green LED (non PWM pin)
  digitalWrite(P_GREEN_LED, on ? HIGH : LOW);
}

void flash_red()
{
  // flash the red light
    if ((millis() - red_led_flash) > 200)
    {
      red_led(!red_led_flash_on);
      red_led_flash_on = !red_led_flash_on;
      red_led_flash = millis();
    }
}

double predict_current()
{
  // predict current given volume, pressure parameters
  // empirically determined formula
  uint16_t v = nom_vals[0][age_state] + val_inc[0][age_state] * pot_vals[0];
  uint8_t p = nom_vals[1][age_state] + val_inc[1][age_state] * pot_vals[1];
  return -1.041041e3 + 2.35386*v + 2.316309e-3*pow(v, 2) - 3.887507e1*p + 7.7198644*pow(p, 2) - 4.2099326e-2*v*p;
}

void update_current()
{
  // read the current value from the sensor, add it to the total sum
  uint16_t potentiometer_raw = analogRead(P_CURRENT);
  double voltage_raw =   (5.0 / 1023.0)* analogRead(VIN);// Read the voltage from sensor
  voltage =  voltage_raw - QOV + 0.012 ;// 0.000 is a value to make voltage zero when there is no current
  double current = voltage / sensitivity[MODEL] * -1; // sensor is flipped
  current_sum += current;
}

void setup() {
  // Setup code
  Serial.begin(9600);
  pinMode(P_RED_LED, OUTPUT);
  pinMode(P_GREEN_LED, OUTPUT);
  pinMode(P_SETTING_BUTTON, INPUT_PULLUP);
  pinMode(P_START_BUTTON, INPUT_PULLUP);
  servo.attach(P_SERVO);
  servo.write(map_servo_pos(START_POS)); // home the servo
  lcd.init();
  lcd.backlight();
  lcd_startup();
  red_led(true);
  green_led(true);
  delay(3000);
  lcd_init();
  green_led(false);
}


///////////////////////////// MAIN /////////////////////////////


void loop() {
  // Just some button debouncing here
  if (!can_read_age_button && millis() - age_button_time >= 500) {
    can_read_age_button = true;
  }
  if (!can_read_start_button && millis() - start_button_time >= 500) {
    can_read_start_button = true;
  }
  
  // If the user isn't being warned, update potentiometer values
  // If ventilation isn't occuring, update age setting
  if (!warn_user)
  {
    if (!ventilating)
    {
      check_age_setting();
    }
    check_pot_vals();
  }
  
  // if halted during a servo movement
  if (halt)
  {
    compression_state = 0;
    ventilating = false;
    drive_servo(map_servo_pos(START_POS));
    release_time = millis();
  }
  halt = check_halt();
  
  if (warn_user)
  {
    flash_red();
  }
  
  if (ventilating)
  {
    uint16_t ms_per_breath = get_ms_per_breath();
    int16_t post_breath_delay = ms_per_breath - base_delays[age_state];
    if (post_breath_delay < 0)
    {
      // just in case
      post_breath_delay = 1000;
    }
    
    if (time_to_squeeze && !compression_state) 
    {
      // squeeze bag
      compression_state = 1;
      uint16_t des_vol = nom_vals[VOL][age_state];
      des_vol += val_inc[VOL][age_state] * pot_vals[VOL];
      uint16_t dest = vol_to_ang(des_vol);
      if (age_state == 0)
      {
        // exaggerate adult compression differences for demo purposes
        // SHOULD PROBABLY REMOVE THIS!!
        // blockage detection needs to be recharacterized if this is removed
        dest = map(dest, 193, 208, 180, 250);
      }
      drive_servo(map_servo_pos(dest));
      squeeze_time = millis();
    }
    else if (time_to_release && compression_state)
    {
      // release bag
      
      // blockage detection
      // ONLY works for adult age group
      if (current_sum >= predict_current() * 1.2 && age_state == 0)
      {
        halt = true;
        green_led(false);
        warn_user = true;
        lcd_warn();
      }
      else
      {
        compression_state = 0;
        drive_servo(map_servo_pos(START_POS));
        release_time = millis();
      }
      current_sum = 0;
    }
    
    if (compression_state)
    {
      update_current();
    }
    
    time_to_squeeze = millis() - release_time > post_breath_delay;
    time_to_release = millis() - squeeze_time > base_delays[age_state];
  }
  
}

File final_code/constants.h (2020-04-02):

// pin layout
#define P_START_BUTTON 4
#define P_SETTING_BUTTON 5
#define P_CURRENT 0
#define P_VOL_POT 1
#define P_PRESS_POT 2
#define P_RATE_POT 3
#define P_RED_LED 6
#define P_GREEN_LED 8
#define P_SERVO 10

// array indices
#define VOL 0
#define PRES 1
#define RATE 2

// measured physically, was stated to be 270 though
#define MAX_SERVO_POS 250
#define START_POS 0

// these speeds correspond to delays
// i.e higher delay, slower speed
#define MIN_SPEED 10
#define MAX_SPEED 0

// current sensor constants
#define VIN A7
#define VCC 5.0
#define MODEL 2
#define QOV 0.5 * VCC

// potentiometer offset values
#define POT_PIN_OFFSET 1
#define POT_LCD_OFFSET 1

// x-coordinate of numeric values on LCD
#define LCD_H_SPACING 13

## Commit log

2020-02-01 added some code that moves the motor based on encoder values
2020-02-06 add servo testing and simple squeezing code
2020-04-02 reorganized final code, added current sensor characterization
    [current_data.xlsx]
2020-04-03 reorganize stuff, remove all outdated code
    [current_data.xlsx]
2020-04-05 update readme, add software flowchart
2020-04-06 Upload of CAD files and Assembly Instructions
    [Back Support Assembly.SLDASM, Back Support Feet.SLDPRT, Back Support Layer.SLDPRT, Bag Pullout Support.SLDPRT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]
2020-04-06 Update to Assembly Instructions
2020-04-06 Update to assembly Instrucitons
